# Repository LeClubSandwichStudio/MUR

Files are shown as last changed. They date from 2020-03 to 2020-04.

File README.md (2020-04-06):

# M.U.R
Minimal Universal Respirator

For more general informations about this project, see https://www.mur-project.org/

This project is under [GPLv3] (https://www.gnu.org/licenses/gpl-3.0.en.html)

## 01_MUR_OVERVIEW

Contains general documentation about the project.

## 02_MUR_HARDWARE

Contains all hardware related documentations: models, wiring, exploded views, etc

## 03_MUR_SOFTWARE

Contains Arduino based code source for the controler.

## 99_MUR_TESTS

Contains M.U.R bench marks

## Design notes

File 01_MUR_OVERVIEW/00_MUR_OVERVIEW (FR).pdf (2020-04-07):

### Minimal Universal Respirator v0.3

Aperçu général du système
(General Overview)

### INTRODUCTION

Le dispositif MUR se définit comme un équipement de respiration artificielle d'urgence. Il s’adresse au corps médical souhaitant soigner un patient atteint de SDRA (syndrome de détresse respiratoire aiguë).

Un dispositif MUR est composé respectivement d’un système matériel (“hardware”) et d’un système logiciel (“software”), pour fonctionner.

### PRINCIPE FONCTIONNEL

Sources d’entrée d’air variables.
Gestion instantanée de la pression administré au patient, par une gestion synchronisée de “fuites d’air”.

### UTILISATION

Mode ventilatoire d’usage : Pression Contrôlée (PC)

Réglages machines :
- Cycles respiratoires
- Ratio I/E
- Pression de crête
- Pression de plateau
- Pression expiratoire positive

### MATERIEL

Prérequis matériel :
- Alimentation sur secteur en 230V
- Cable usb pour communiquer avec le logiciel (optionnel)

Prérequis logiciel (optionnel, pour test et visualisation sur ordinateur) :
- Disposer d’un ordinateur avec port USB
- Avoir installé le logiciel Arduino

Le dispositif Minimal Universal Respirator (MUR) est constitué de 7 sous-ensembles distincts, qui une fois combinés, constituent le système matériel (“hardware”) d’un MUR :

1. La source d’air (FR) (https://drive.google.com/open?id=1SqGHQjwBfO2f25Swwv3l0SGI28G9KxEalMFHdRkD32M)
2. Le filtre d’entrée d’air et le régulateur de pression courante (FR) (https://drive.google.com/open?id=1I-5K1rnMSs5uvp3ED-RQ1LcxX0brZkwWDnDNk8wLztA)
3. Les valves esclaves (FR) (https://drive.google.com/open?id=1w_EUj4ocEakElgCnpraXDVv3cVOd3zsCE-9gxyla1rs)
4. Les systèmes de captations (FR) (https://drive.google.com/open?id=1ARKAw2D5dZf-3HR5xr1Ms6IWQ_QXqz-S4Hy4_T1l_os)
5. Les adaptateurs (FR) (https://drive.google.com/open?id=1K2FceapsPLCinnWBYBrEqLem5kVpyN8-s0TL2MW7GUM)
6. Le panneau de contrôle (FR) (https://drive.google.com/open?id=1XikZ0ODiRMPeeytIIQJwRYhBmEAExoJSR04DGwt4p20)
7. La tuyauterie/plomberie (FR) (https://drive.google.com/open?id=1fXODXtvYolFTmdxDlxn4JihmsS-h_IIxJIVhl_Bkw6E)

Légende (pdf)

NAME | WHAT
B Poumon de test

T Tuyaux medicaux

C1 | Capteur Pression Entrée Patient
C2 | Capteur Pression Athmosphérique
V1 | Valve esclave Entrée
S1 | Servomoteur de V1
V2 | Valve esclave Sortie
S2 | Servomoteur de V2
V3 | Valve Ressort (Echappement)
F1 | Filtre entrée D'air
CP | Paneau de contrôle

M Monitoring

A1 | Adaptor 1
A2 | Adaptor 2
A3 | Adaptor 3
FL1 | Flange 1
FL2 | Flange 2
FL3 | Flange 3

T Transformateur
Y Y

IN0 Arrivée d'air Continue

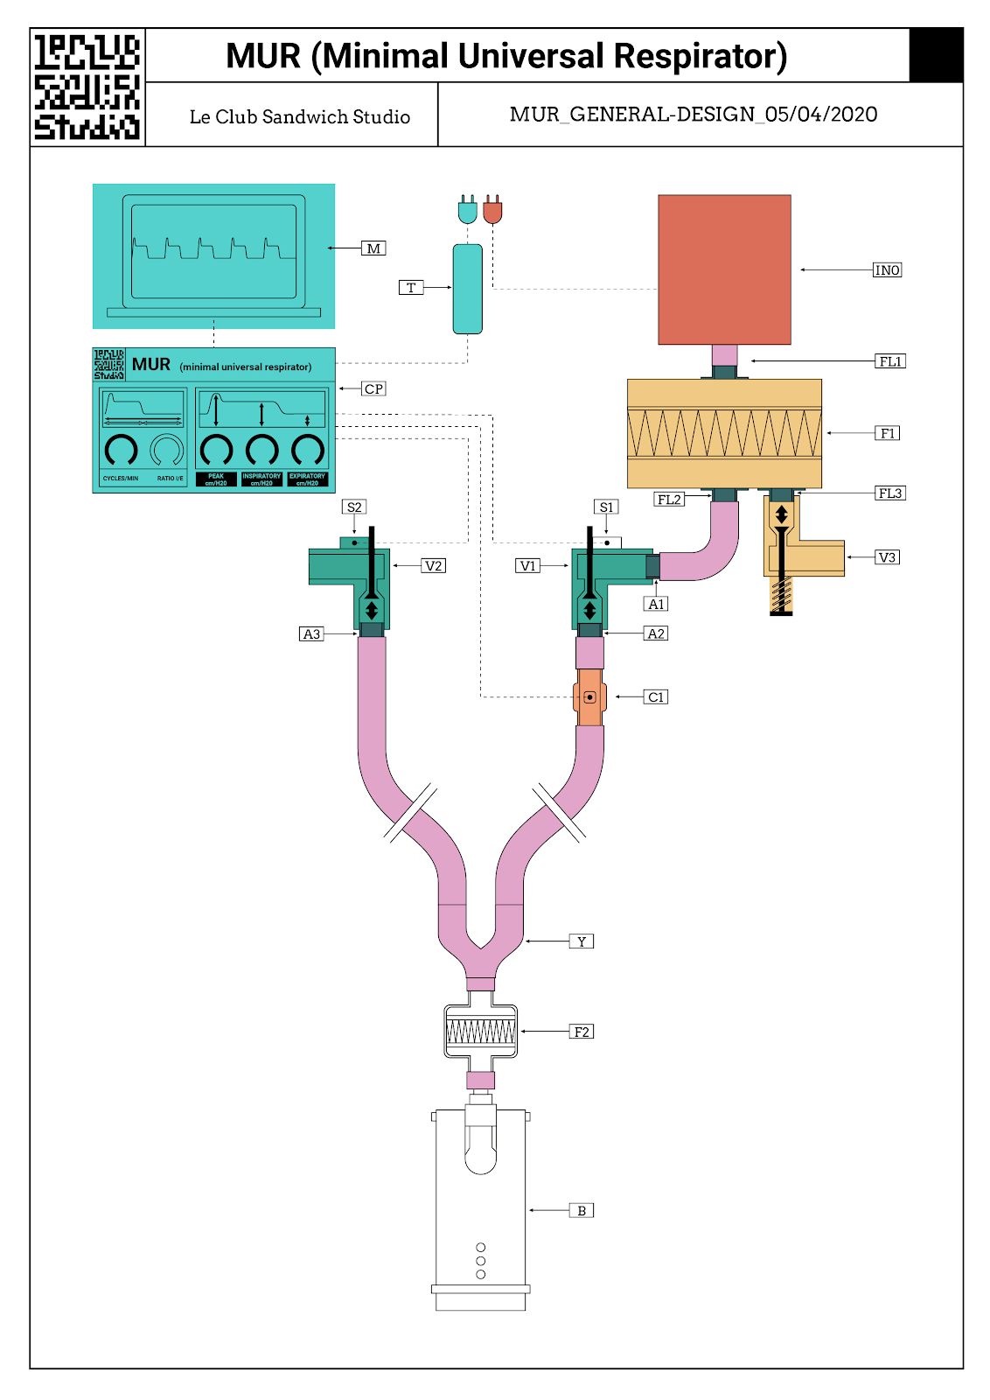
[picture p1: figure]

Design général des blocs fonctionnels (pdf) (https://drive.google.com/open?id=1_WcDWkCbM0ZlqO23SKp42NGnG-bO8ovX)

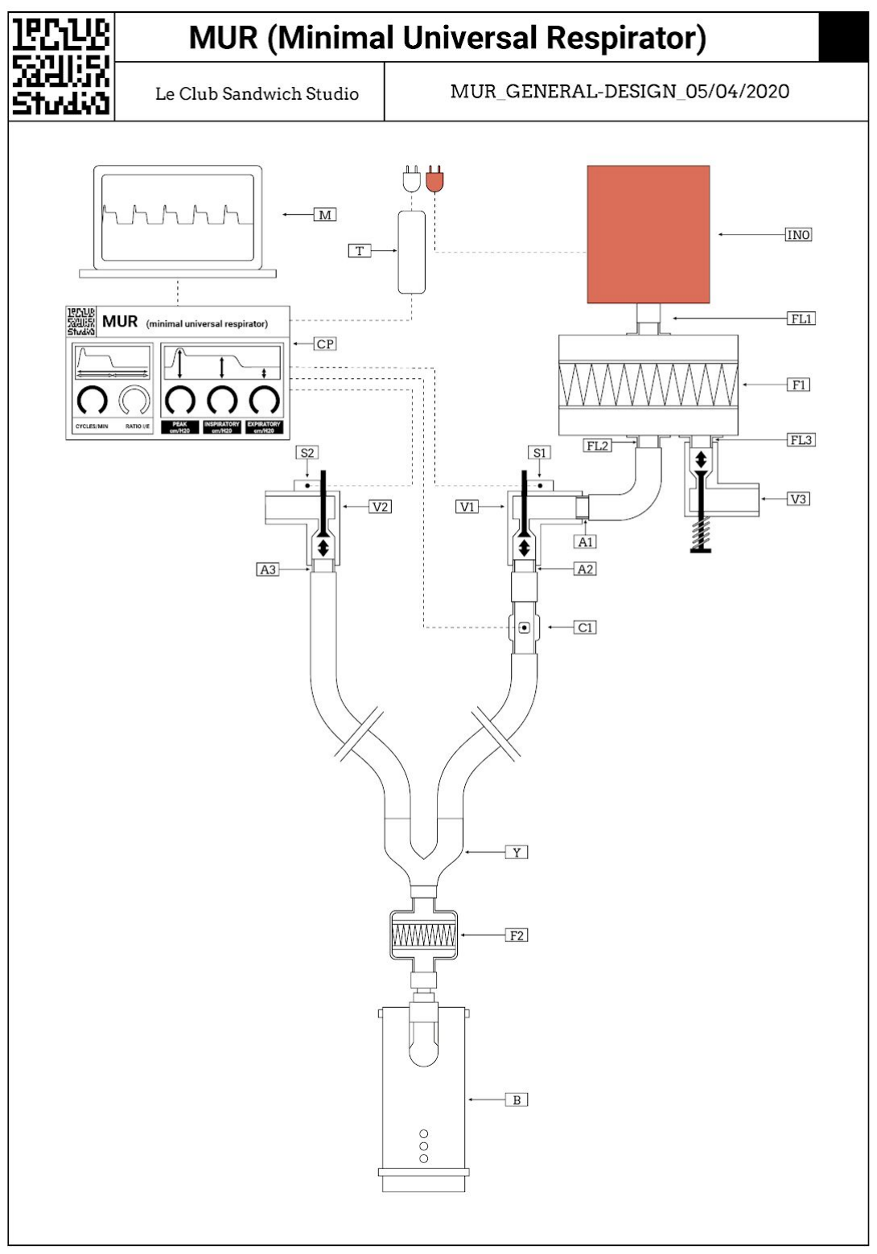
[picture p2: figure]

Design général - sous-ensemble 1 : source d’air (pdf) (https://drive.google.com/open?id=1FOaVzaCyhG92lL_MXu_-5X0B1L0EyU57)

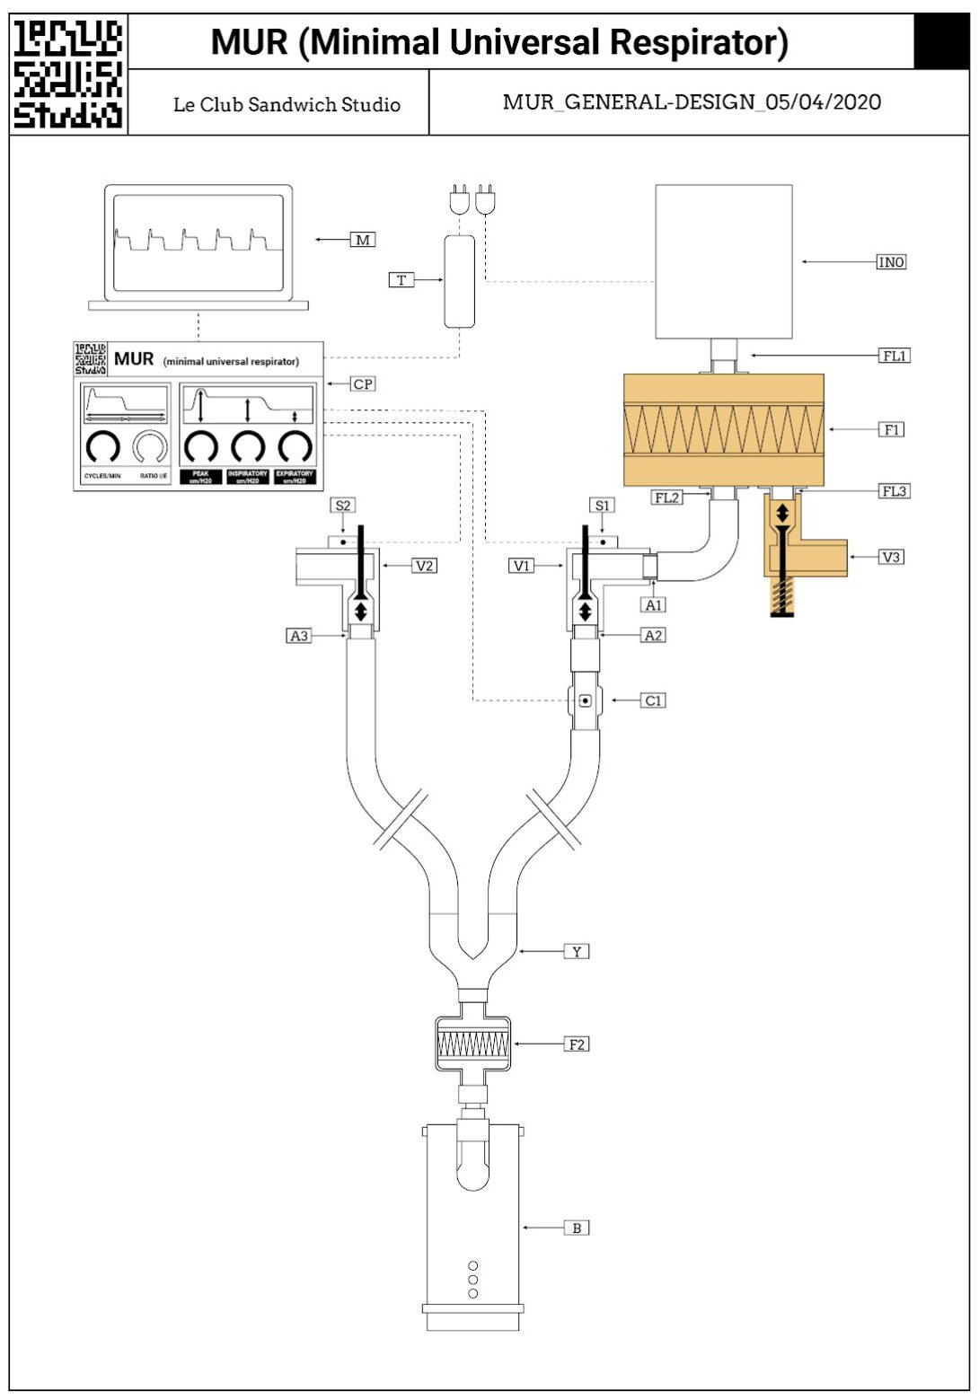
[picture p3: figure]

Design général - sous-ensemble 2 : filtre (pdf) (https://drive.google.com/open?id=1hKSTGPQz4cmegmwHS-HlvNu4kxHyBkxj)

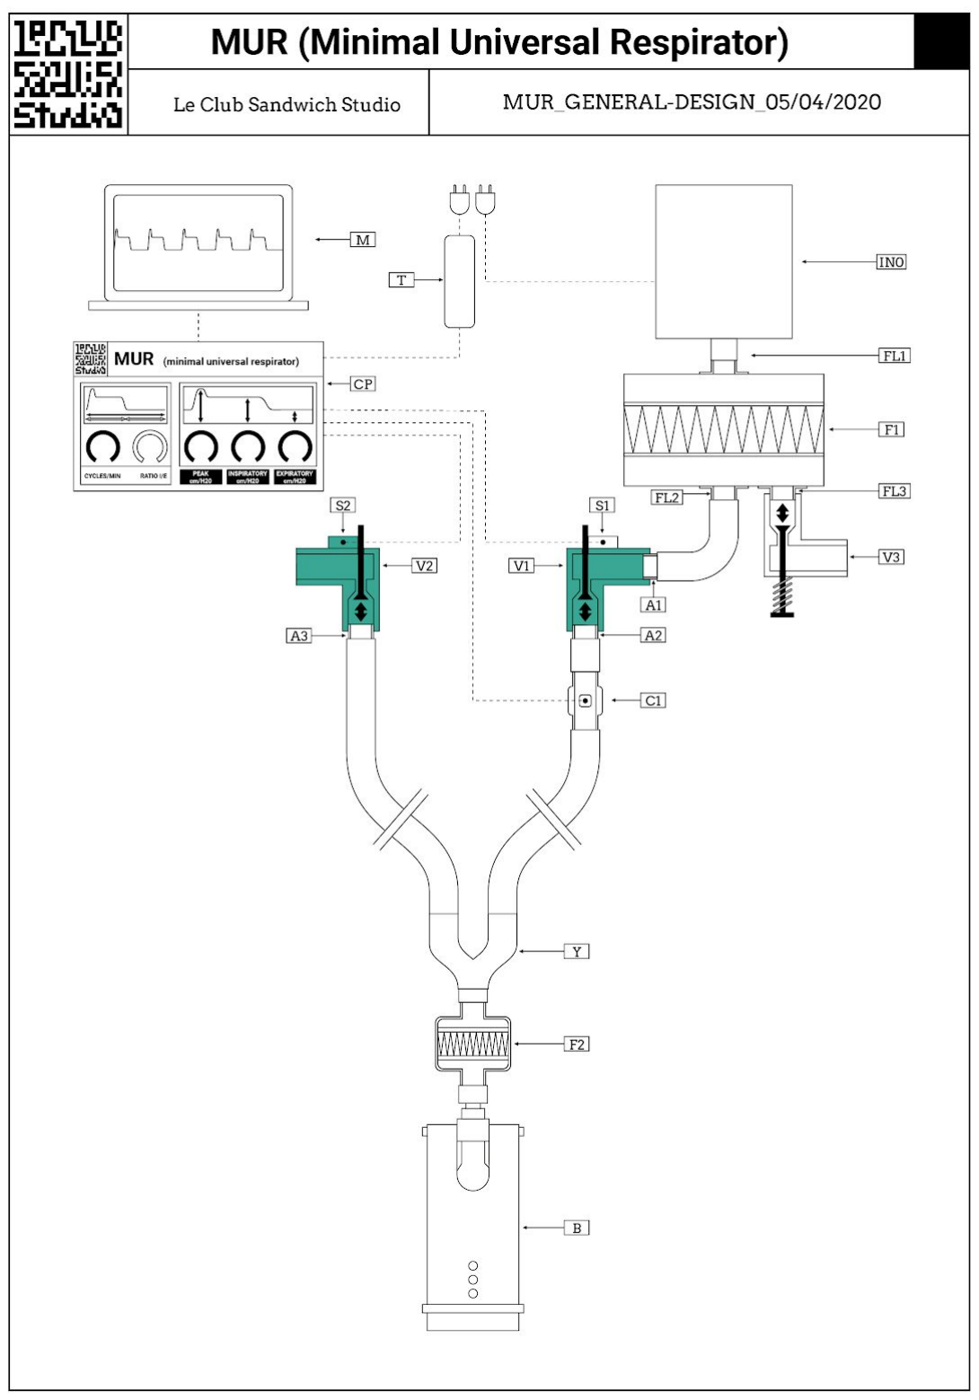
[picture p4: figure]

Design général - sous-ensemble 3 : valves (pdf) (https://drive.google.com/open?id=1HCkXBzR4LwH6LnuTaRVHANtpQzyrADqG)

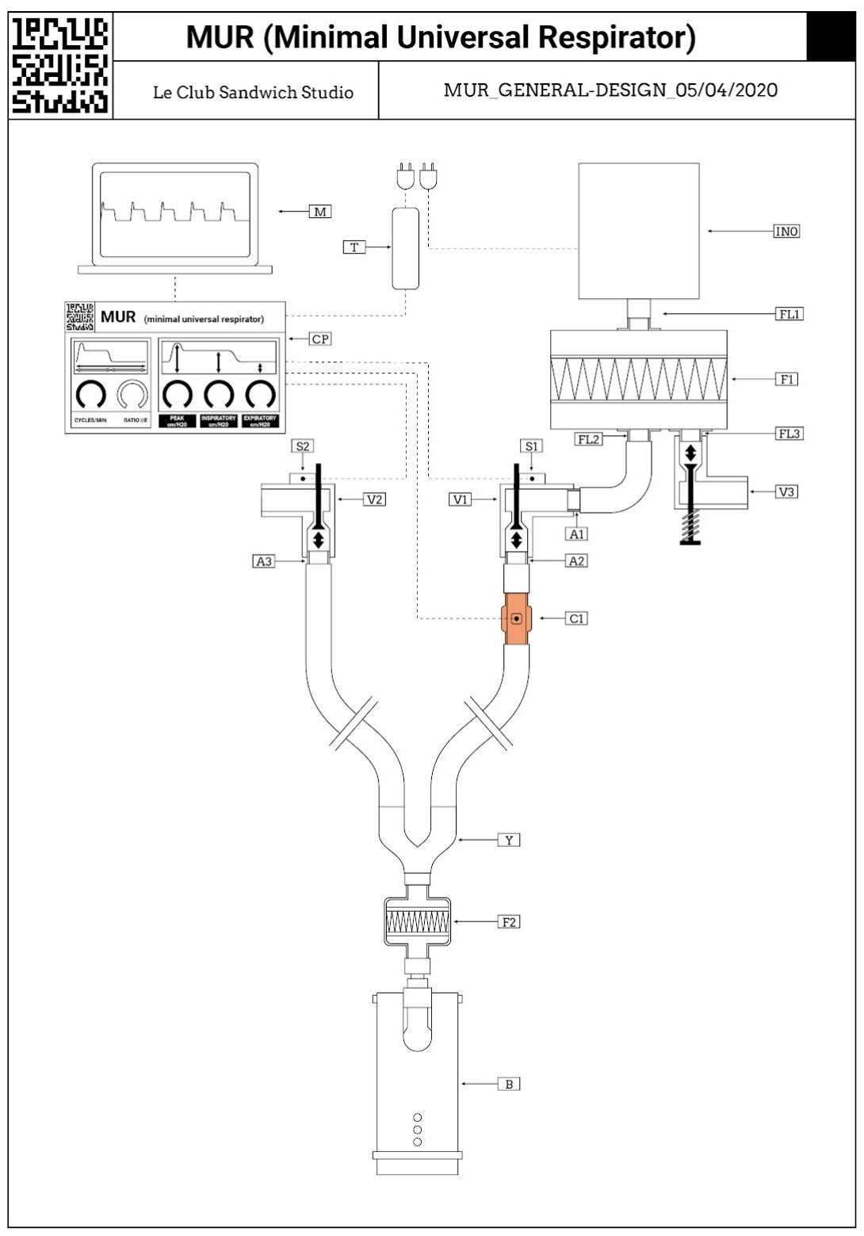
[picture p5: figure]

Design général - sous-ensemble 4 : captation (pdf) (https://drive.google.com/open?id=1NCK5aFOVgX5Ek2YtG8QKx2trs72YkA_k)

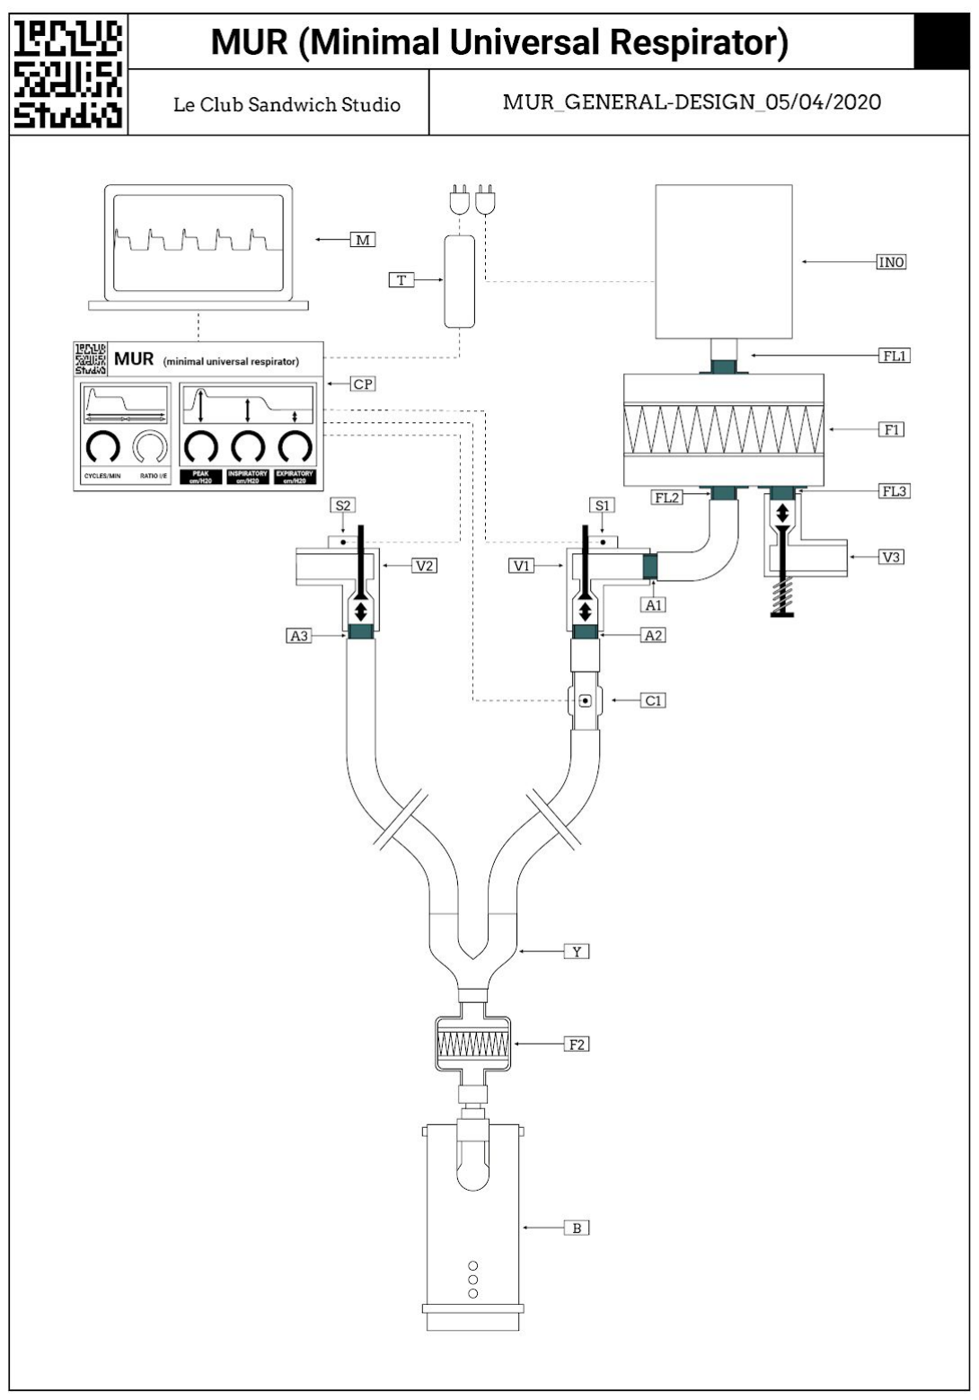
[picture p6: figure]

Design général - sous-ensemble 5 : adaptateurs (pdf) (https://drive.google.com/open?id=1cCQLFfMAgoJG9c6c1g39FGafxrEThaiq)

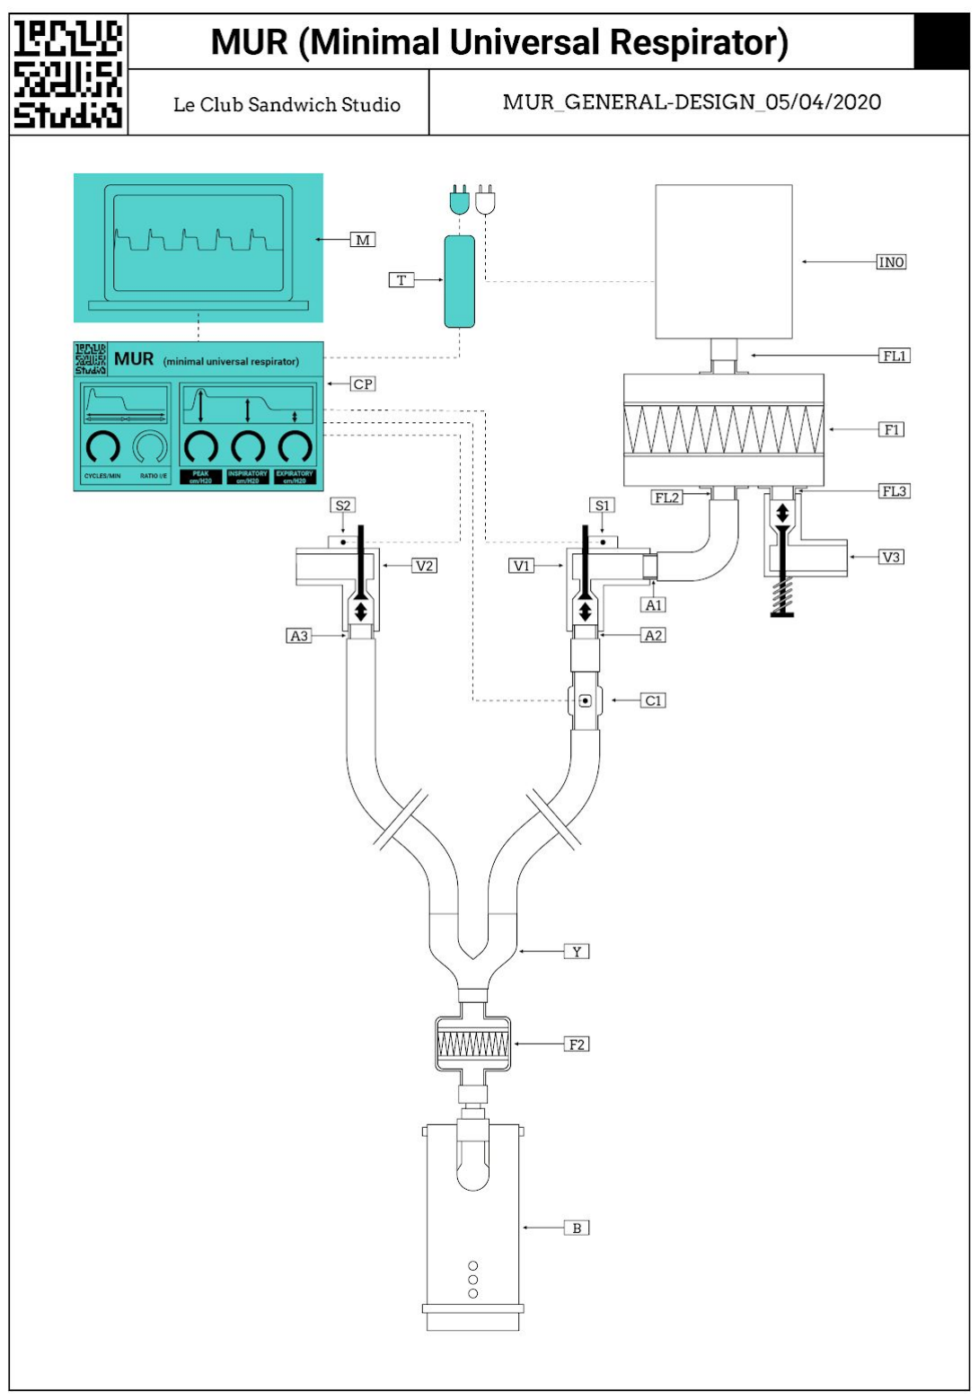
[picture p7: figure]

Design général - sous-ensemble 6 : panneau de contrôle (pdf) (https://drive.google.com/a/leclubsandwich.studio/file/d/18ofSSI9X4tlmFmg1ObH6QxRjyoEKfB24/view?usp=sharing)

### FLUX D’AIR

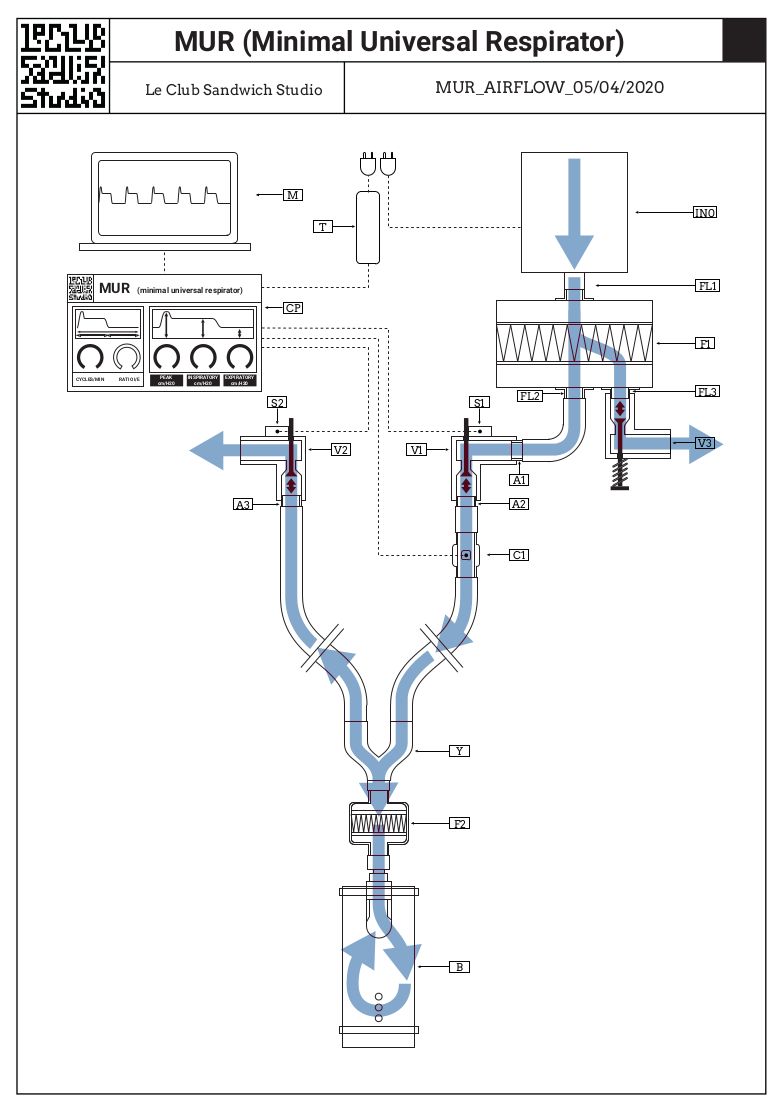
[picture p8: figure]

### LOGICIEL

### Explication fonctionnelle du code Arduino

### Présentation Générale :

Le code se veut simple, adaptable et surtout le plus stable possible.
Dans cette première version il permet des réglages de respiration qui sont les mêmes que les réglages utilisé par le corps médical. Le but n’est pas de faire preuve d’innovation à ce sujet mais d’accompagner les soignants au plus proche de leurs connaissances.

### Fonctionnalités :

Un code Arduino, simple et efficace apte à ventiler une personne sédaté dans une structure permettant d’accueillir des malades Covid-19. Code largement commenté directement sur Arduino.

- Cinqs potentiomètres pour simplement et précisément régler le cycle de respiration
- Cycles par minute
- Ratio Inspiration/Expiration (I/E)
- Pression peak a l’inspiration
- Pression plateau pendant l’inspiration
- Pression PEEP pendant l’expiration
- Deux interrupteurs à glissière pour des fonctions de réglage et de maintenance
- Maintenance pour mettre les deux servos à 0° (position fermé) pour le montage
- Calibration pour régler la pression maximale dans le circuit
La routine de réglage des valves et de la pression est détaillé dans le code Arduino.
- Deux capteurs de température/pression/humidité d’air bosch BME280.
- Dans le circuit d’air après la valve d'entrée (C1)
- Un deuxième capteur pour la pression atmosphérique ambiant (C2)

- “Monitoring” à travers le traceur serial inclue dans la Arduino IDE. Ce logiciel est gratuit et existe pour quasiment tous les systèmes d’exploitation au monde.
- Pression dans le circuit d’air (bleu en CmH20)
- Position de la valve d’entrée
- Position de la Valve de sortie
- Alarme qui réagit & la suppression. (buzzer et led)
- peakAlarmLevel = 40mbar
- plateauAlarmLevel = 30mbar

### SCHEMA DE CABLAGE

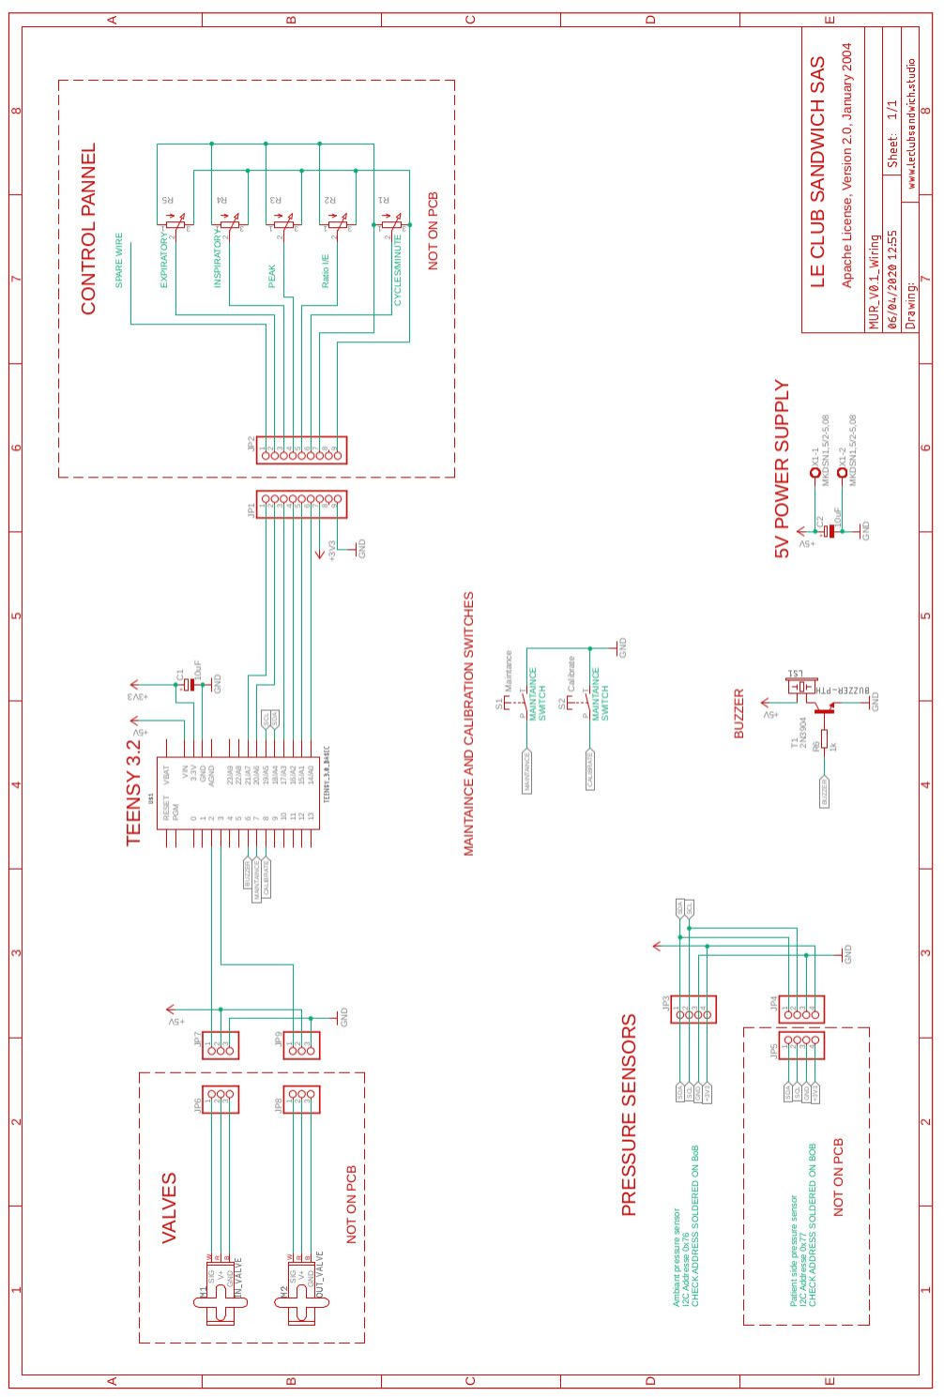
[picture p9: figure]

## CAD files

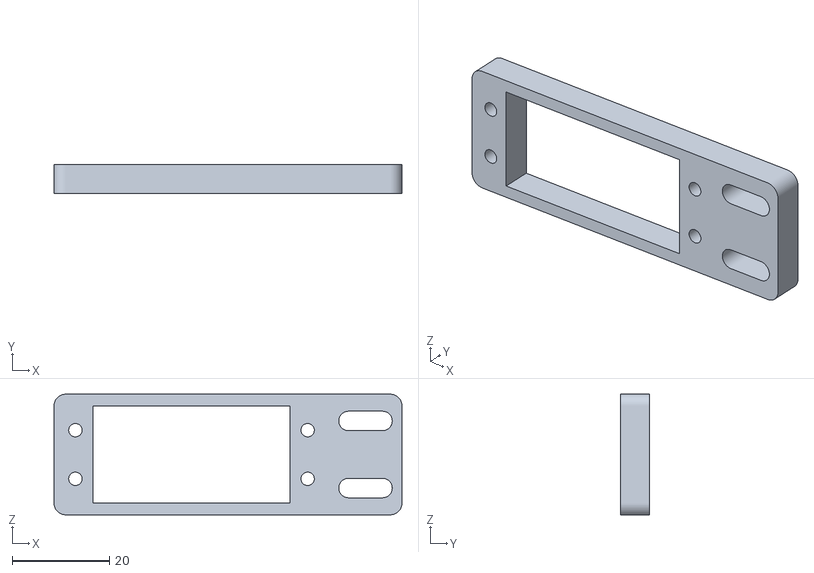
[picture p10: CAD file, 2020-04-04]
02_MUR_HARDWARE/models/v0.3/ServoHolder.stl
71.5 x 6.00 x 24.8

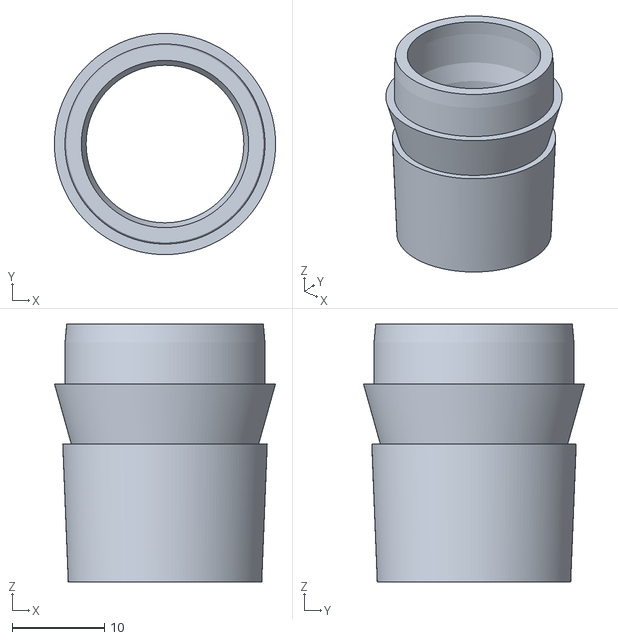
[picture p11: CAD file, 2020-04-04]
02_MUR_HARDWARE/models/v0.3/Adaptor_X2.stl
24.0 x 24.0 x 28.0

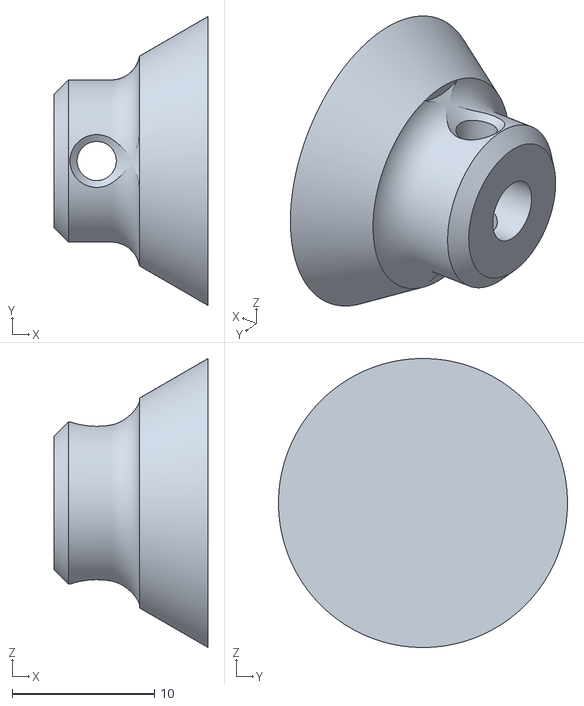
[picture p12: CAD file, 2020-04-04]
02_MUR_HARDWARE/models/v0.3/Valve_Piston.stl
10.8 x 20.3 x 20.3

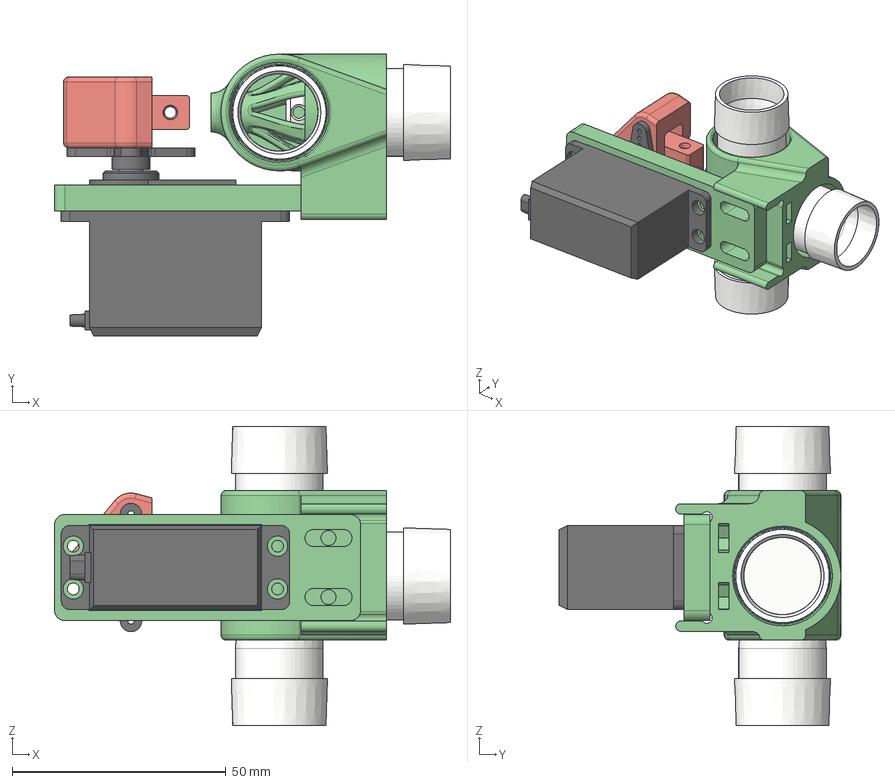
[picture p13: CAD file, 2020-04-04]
02_MUR_HARDWARE/models/v0.3/ValveV3.1 v5.step
92.6 x 65.9 x 70.0 mm

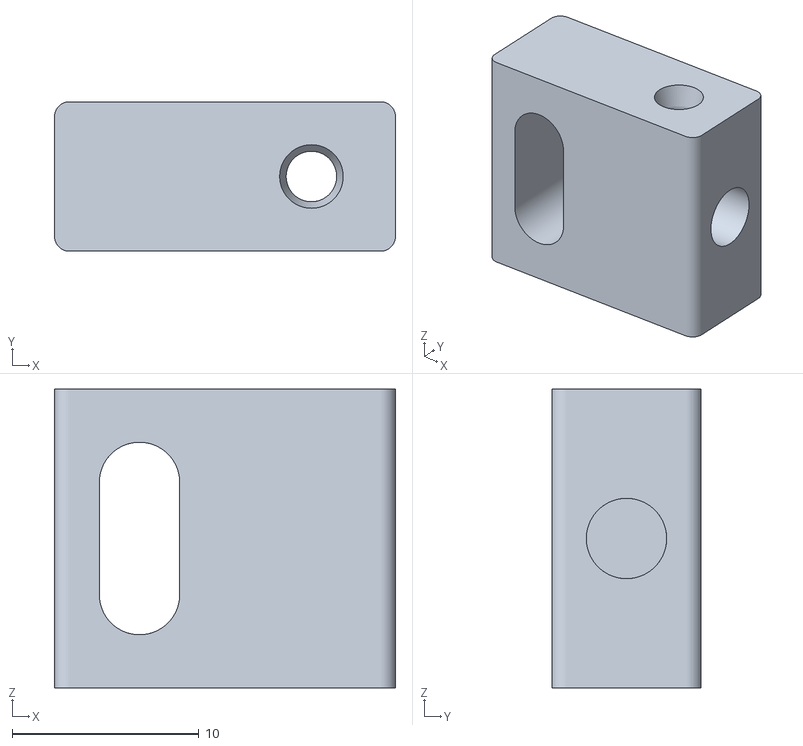
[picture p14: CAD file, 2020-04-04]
02_MUR_HARDWARE/models/v0.3/Valve_Pusher.stl
18.2 x 8.00 x 16.0

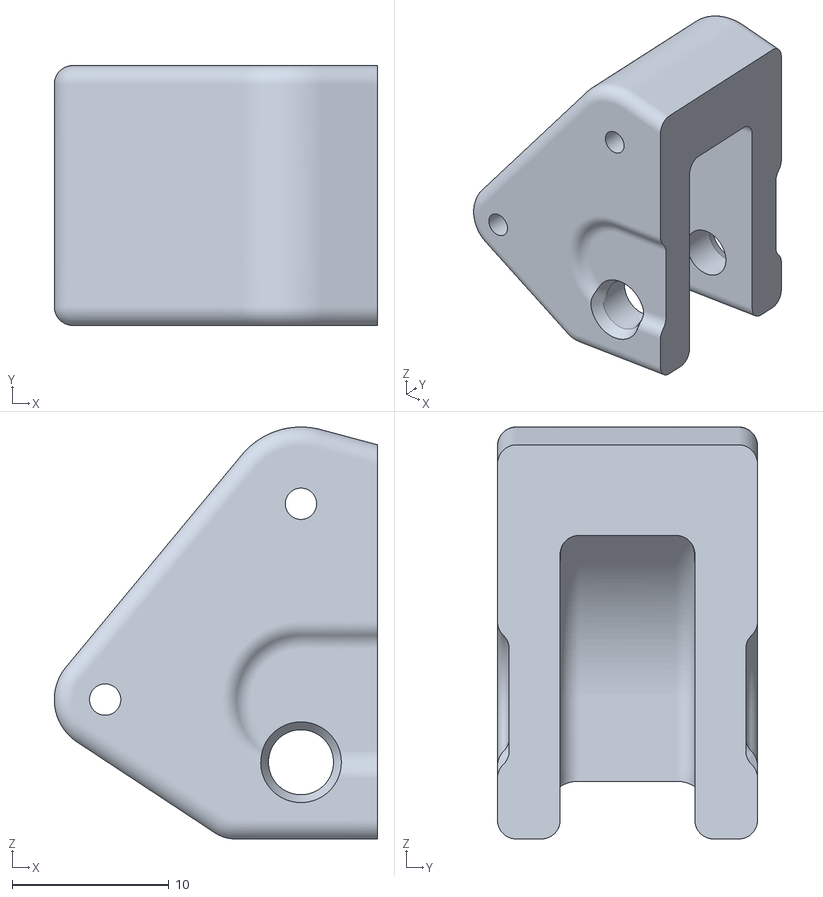
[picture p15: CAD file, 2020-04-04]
02_MUR_HARDWARE/models/v0.3/Servo_Lever.stl
20.7 x 16.6 x 26.3

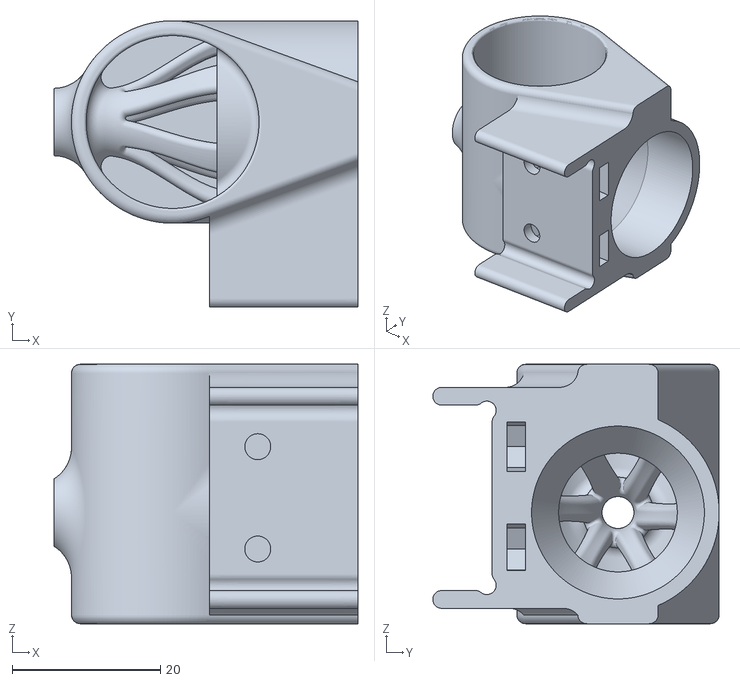
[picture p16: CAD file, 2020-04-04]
02_MUR_HARDWARE/models/v0.3/Valve_Body.stl
41.0 x 38.6 x 35.0

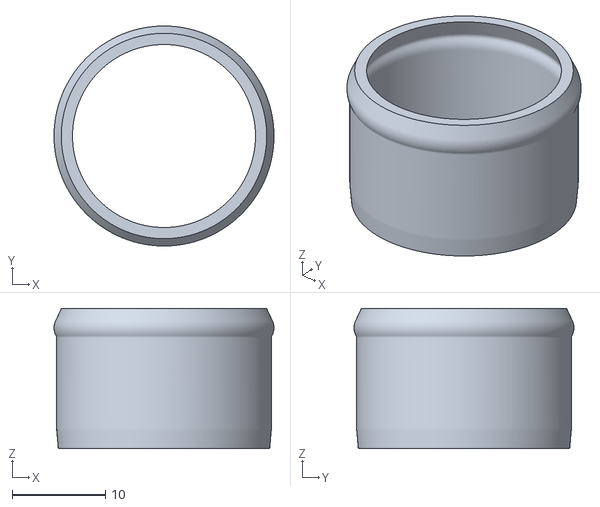
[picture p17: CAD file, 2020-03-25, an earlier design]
02_MUR_HARDWARE/models/v0.1/3D_ExportSTL/Adaptor_X3.stl
23.6 x 23.6 x 15.0

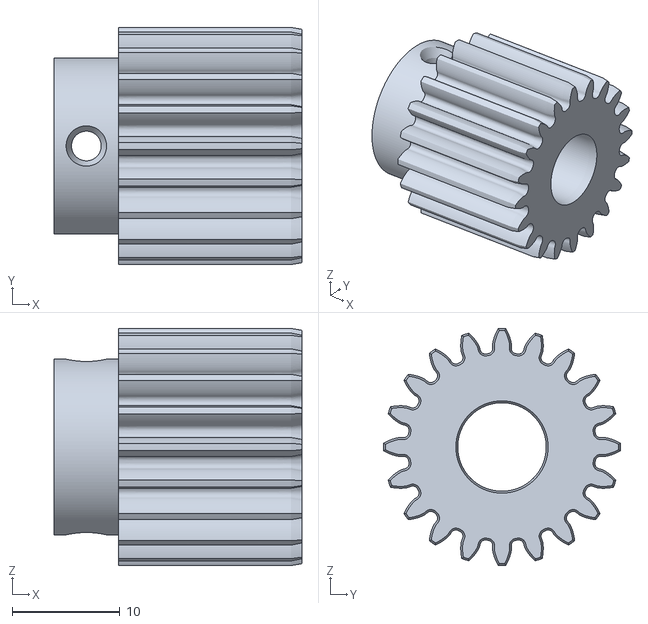
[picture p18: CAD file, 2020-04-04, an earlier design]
02_MUR_HARDWARE/models/v0.2.1/Pinion_20.stl
23.0 x 22.0 x 22.0

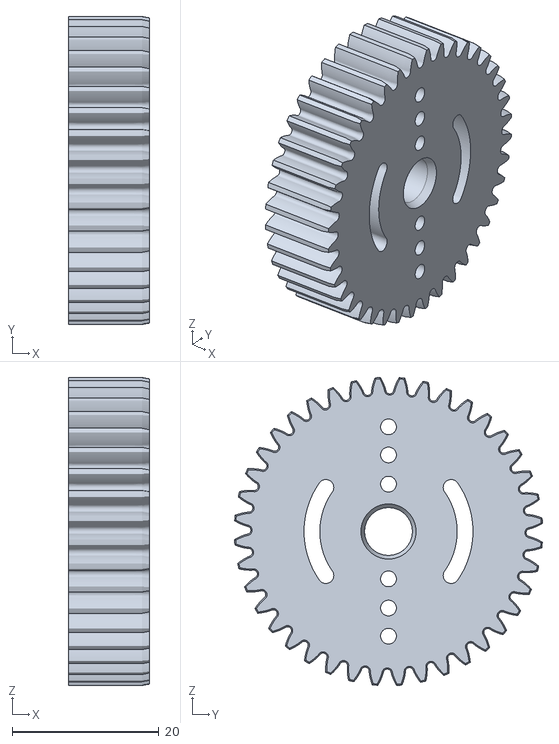
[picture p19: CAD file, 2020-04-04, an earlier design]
02_MUR_HARDWARE/models/v0.2.2/Spur_40.stl
11.0 x 41.9 x 41.9

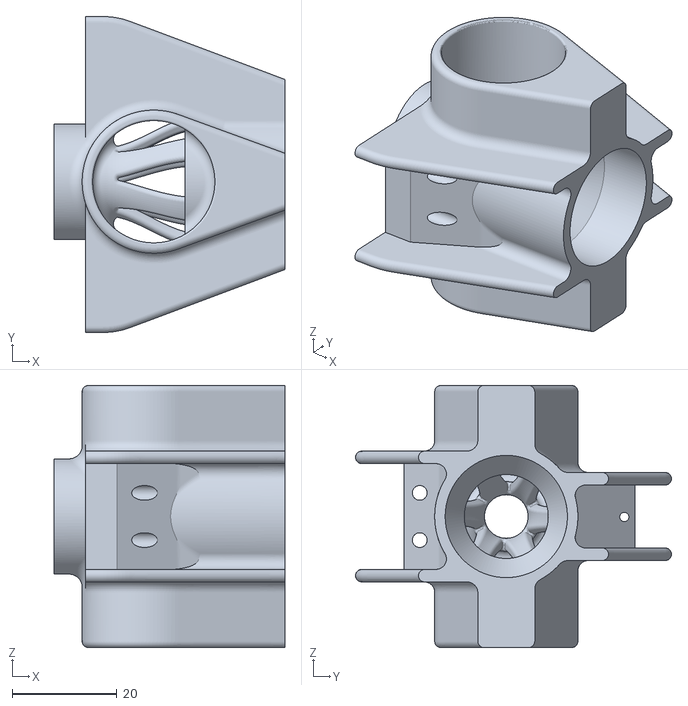
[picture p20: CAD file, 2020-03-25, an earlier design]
02_MUR_HARDWARE/models/v0.1/3D_ExportSTL/Valve_Body.stl
44.0 x 60.2 x 50.0

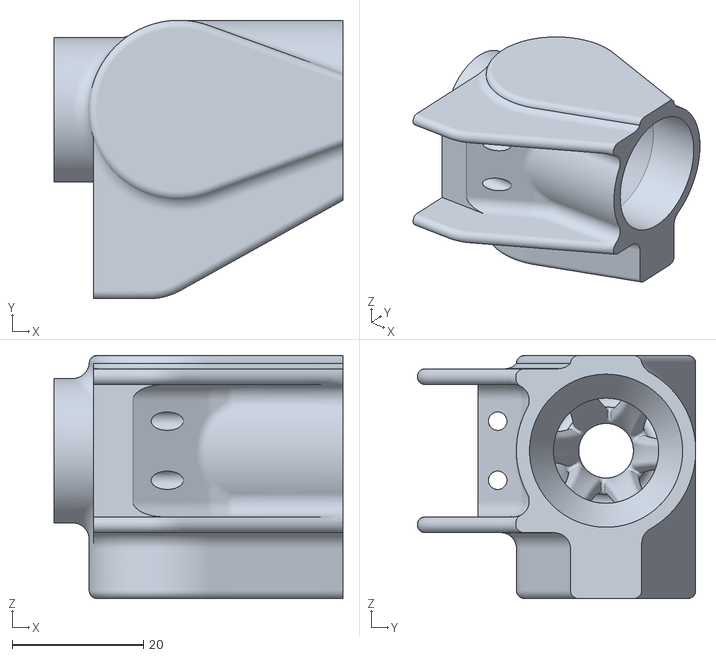
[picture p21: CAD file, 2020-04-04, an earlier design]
02_MUR_HARDWARE/models/v0.2.1/Valve_Body.stl
44.0 x 42.4 x 37.0

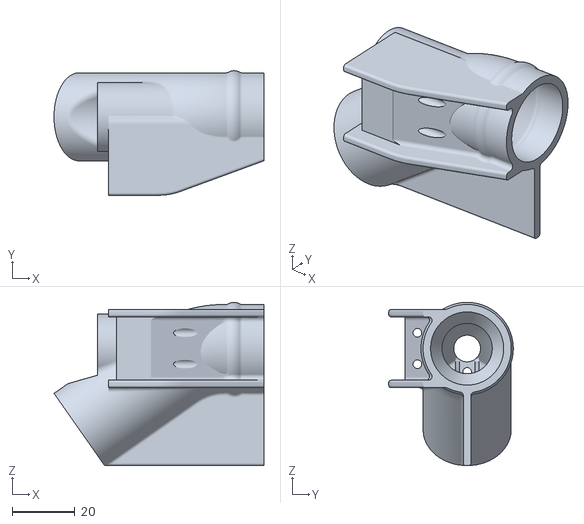
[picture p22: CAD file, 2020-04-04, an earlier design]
02_MUR_HARDWARE/models/v0.2.2/Valve_Body 2.2.stl
66.9 x 39.7 x 52.0

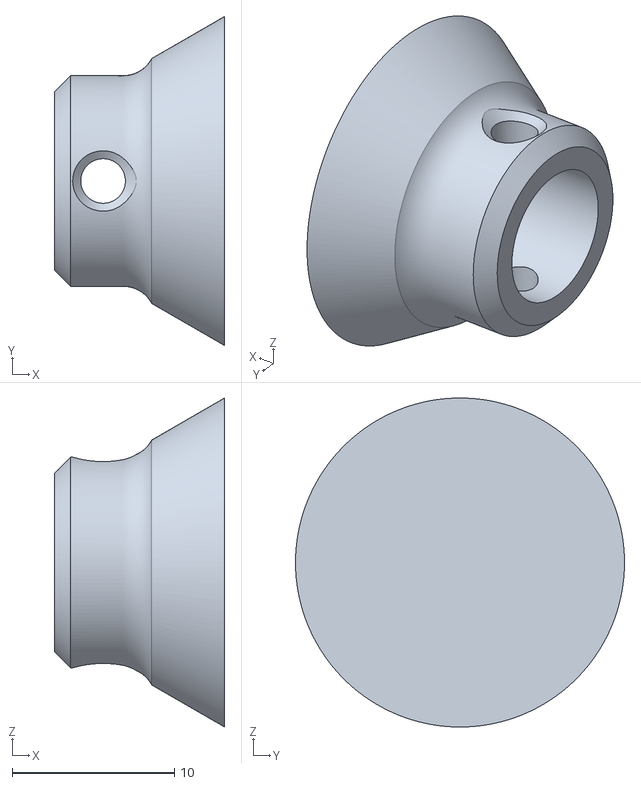
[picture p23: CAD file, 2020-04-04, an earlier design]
02_MUR_HARDWARE/models/v0.2.2/Valve_Piston.stl
10.5 x 20.3 x 20.3

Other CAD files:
02_MUR_HARDWARE/models/v0.1/3D_ExportSTL/Spur_40.stl
02_MUR_HARDWARE/models/v0.2.1/Spur_40.stl
02_MUR_HARDWARE/models/v0.1/3D_ExportSTL/Pinion_20.stl
02_MUR_HARDWARE/models/v0.2.1/Valve_Piston.stl
02_MUR_HARDWARE/models/v0.1/3D_ExportSTL/Valve_Piston.stl
02_MUR_HARDWARE/models/v0.2.2/Pinion_20.stl
02_MUR_HARDWARE/models/v0.2/V2.0_MetalScrew/Adaptor_X3.stl
02_MUR_HARDWARE/models/v0.2/V2.0_MetalScrew/Spur_40.stl
02_MUR_HARDWARE/models/v0.2/V2.0_MetalScrew/Valve_Body.stl
02_MUR_HARDWARE/models/v0.2/V2.0_MetalScrew/Valve_Piston.stl
02_MUR_HARDWARE/models/v0.2/V2.0_MetalScrew/Valve_Piston_Oring.stl
02_MUR_HARDWARE/models/v0.2/V2.0_PrintedScrew/Adaptor_X3.stl
02_MUR_HARDWARE/models/v0.2/V2.0_PrintedScrew/Pinion_20.stl
02_MUR_HARDWARE/models/v0.2/V2.0_PrintedScrew/Spur_40.stl
02_MUR_HARDWARE/models/v0.2/V2.0_PrintedScrew/Valve_Body.stl
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

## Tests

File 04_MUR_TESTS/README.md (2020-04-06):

This folder contains tests done on bench test equipment by bio-medical engineers.

Date and location is contained in the sub-folder names.

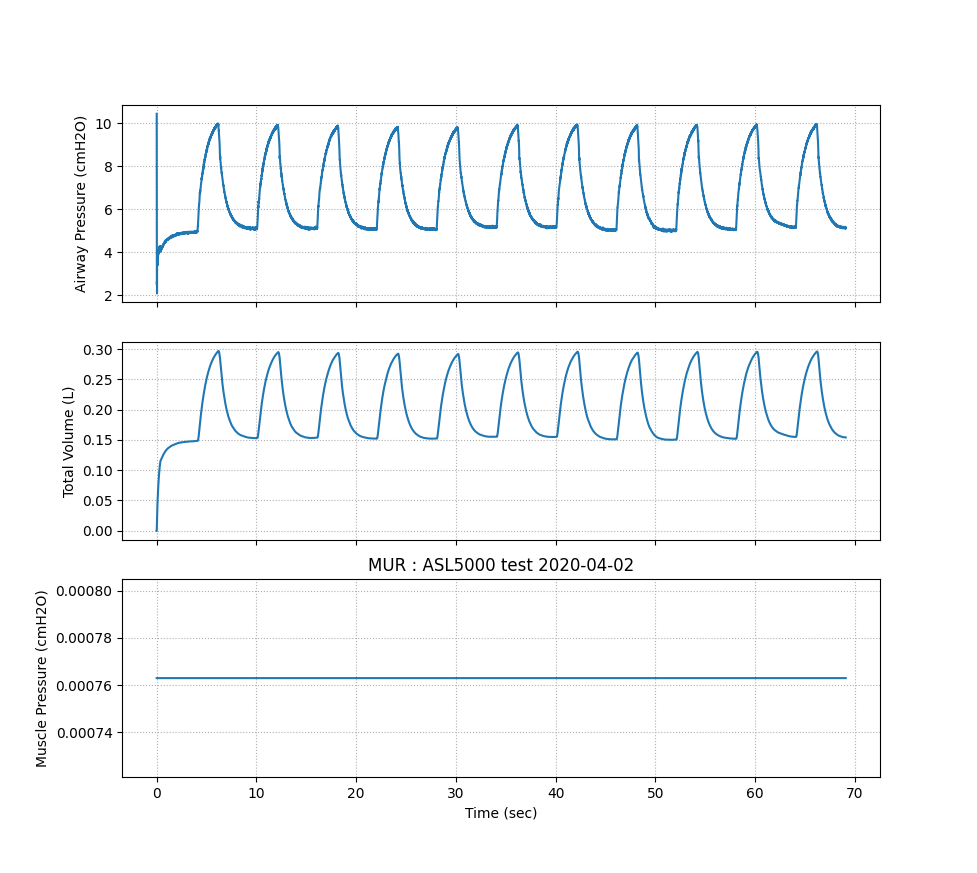
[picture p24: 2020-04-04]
04_MUR_TESTS/2020-03-27-ASL5000-Mondor/test_2.png

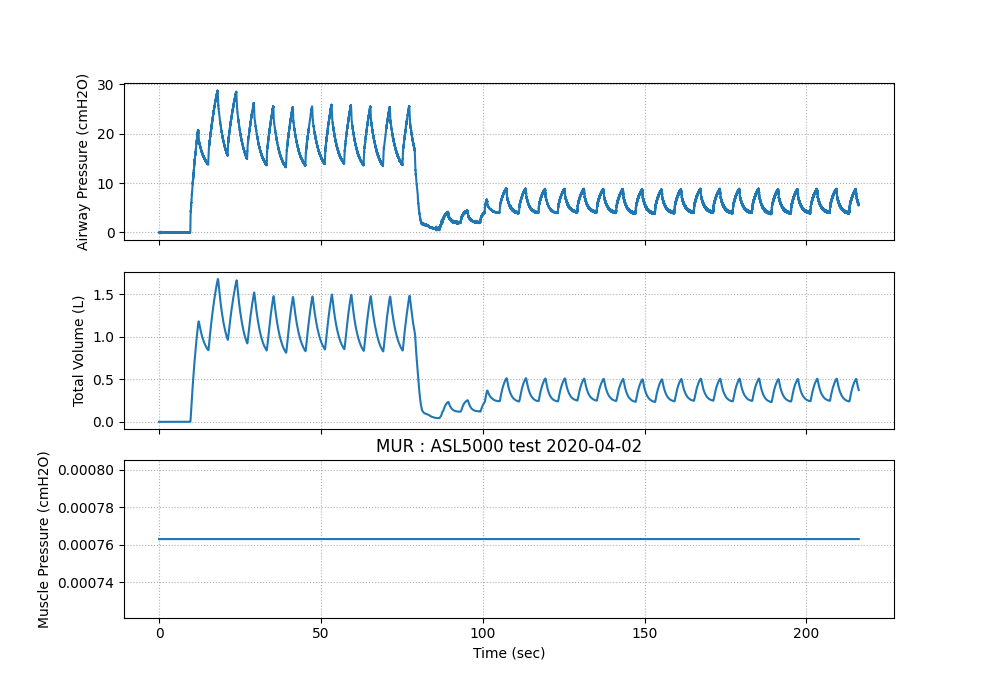
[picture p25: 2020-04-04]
04_MUR_TESTS/2020-03-27-ASL5000-Mondor/test_1.png

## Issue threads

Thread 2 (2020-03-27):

### ISSUE TITLE
In the first comment there seem to be a typo between 180 and 160

### ISSUE THREAD

**Issue by MCMic** [LeClubSandwichStudio/MUR#2]
Maybe I misunderstood but it seems to me lines 52/53 should state 180 like the ones before and after, or the other ones are wrong and should state 160 as well, not sure?

https://github.com/LeClubSandwichStudio/MUR/blob/d80a23c6057c3697014bc0ded8df49dc8f256d1d/V0/software/MUR.ino#L52

**Comment by LeSuedois** [comment]
Hello,
sorry but this value is still in work in progress. We started with 180° and lowered it to 60° now with our new (and better) airvalves. another positive aspect is that the movement is much faster and reduced wear on those cheap servos. 
As written in the comments this value changes from servo to servo and must be tweaked to match your hardware!

**Comment by LeSuedois** [comment]
please wait for major update coming this weekend. we only publish once tested in medical environment

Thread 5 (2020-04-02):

### ISSUE TITLE
compatibility issues with .stl files

### ISSUE THREAD

**Issue by DelphineRoy** [LeClubSandwichStudio/MUR#5]
Could not read the .stl files on my version of cura (4.1.0). They should be readable with any version. Couldn't open it with Windows' stl reader either, nor with sketchup. Windows 3D Builder returned the message "Couldn't load that. Error code: 0x80004005".

**Comment by LeSuedois** [comment]
hmm we don't have problems with our stl files under fusion 360 and prusa slicer...
Many people with other softwares printed out files without problem. I think the problem is on your side, so I close this issue.
Please try with other software. Sketchup is marvelous for "big" stuff and architecture!

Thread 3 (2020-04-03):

### ISSUE TITLE
Maybe you made an error ?

### ISSUE THREAD

**Issue by KennnyTroll** [LeClubSandwichStudio/MUR#3]
Hello!
Maybe you made an error on V0.1 the last argument in the Adafruit_BME280 function
bmePatient.setSampling (1, 1, 3, 1, 1, 10);
and
bmeAmbient.setSampling (1, 1, 3, 1, 1, 10);
because I had to make a modification in your code to bring it to Visual Studio
bmePatient.setSampling (1, 1, 3, 1, 1, 6);
bmeAmbient.setSampling (1, 1, 3, 1, 1, 6);

and visual studio do not accept int values for the setSampling function

I had to replace with

.setSampling (
      Adafruit_BME280 :: sensor_mode :: MODE_FORCED ,// = 1
      Adafruit_BME280 :: sensor_sampling :: SAMPLING_X1 ,// = 1
      Adafruit_BME280 :: sensor_sampling :: SAMPLING_X4 ,// = 3
      Adafruit_BME280 :: sensor_sampling :: SAMPLING_X1 ,// = 1
      Adafruit_BME280 :: sensor_filter :: FILTER_X2 ,// = 1
      Adafruit_BME280 :: standby_duration :: STANDBY_MS_10 //STANDBY_MS_10 = 6      10 not exists !!
      );

For information:
enum standby_duration {
    STANDBY_MS_0_5 = 0b000, // = 0
    STANDBY_MS_10 = 0b110, // = 6
    STANDBY_MS_20 = 0b111, // = 7
    STANDBY_MS_62_5 = 0b001, // = 1
    STANDBY_MS_125 = 0b010, // = 2
    STANDBY_MS_250 = 0b011, // = 3
    STANDBY_MS_500 = 0b100, // = 4
    STANDBY_MS_1000 = 0b101 // = 5
  };

I hope I'm not mistaken, and that it helps you ...

I do not yet have a BME280 sensor to try this code at home but I am trying to create a U-tube manometers with salt water ...

Good luck to all! And thanks for everything !

**Comment by fpistm** [comment]
Hi, 
I confirm the issue raised by @KennnyTroll.
Using enum type is better to ensure to not use a wrong value which is the case here.

**Comment by LeSuedois** [comment]
Thank you guys, indeed I did a mistake...
I try to check this out this afternoon, but most time this week was spent to sourcing parts and talking to people.....
We are in  a hurry since 3 weeks and it's clear that no one in this wokshop is a professional embedded software developer. I only do stuff that works (search for "lesuedois" on google)..
Please feel free to do a pull request if you see stuff I messed up!
This is IMO the fastest way to help me!
Thank you!

**Comment by KennnyTroll** [comment]
Pull requests sent !

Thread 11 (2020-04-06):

### ISSUE TITLE
please

### ISSUE THREAD

**Issue by devoss62** [LeClubSandwichStudio/MUR#11]
Hello,

missing the pusher and a guide piece?

Sylvain,

![ValveV4 0-v40](https://user-images.githubusercontent.com/55943394/78366554-f56db600-75c0-11ea-9673-5c977fea48ad.png)

**Comment by cquest** [comment]
The pusher is not 3D printed. We're about to publish a much more detailed set of documents (WIP).

**Comment by DoubleCigogne** [comment]
These parts are in the BOM and they are not 3D Printed. 
They are :
- T8x4 screw from a 3D printer
- T8x4 Brass nut from a 3D printer

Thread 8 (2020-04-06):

### ISSUE TITLE
Bill of Materials

### ISSUE THREAD

**Issue by Jacoby6000** [LeClubSandwichStudio/MUR#8]
For people to start building these rapidly in local communities, it would be helpful to have a BOM in CSV form which people can reference for when they're gathering supplies.  Here's an example of what I mean:  https://docs.google.com/spreadsheets/d/1Eib0IkmRiP-zVM2p6gZ9PJ2bsDDvSKWbGtUybuFWfcs/edit#gid=1276357080

I'll start working on putting this together in my freetime when I can.

**Comment by LeSuedois** [comment]
Please wait a bit... We are finishing the documentation and update master soon.
BTW, I know what's CSV...

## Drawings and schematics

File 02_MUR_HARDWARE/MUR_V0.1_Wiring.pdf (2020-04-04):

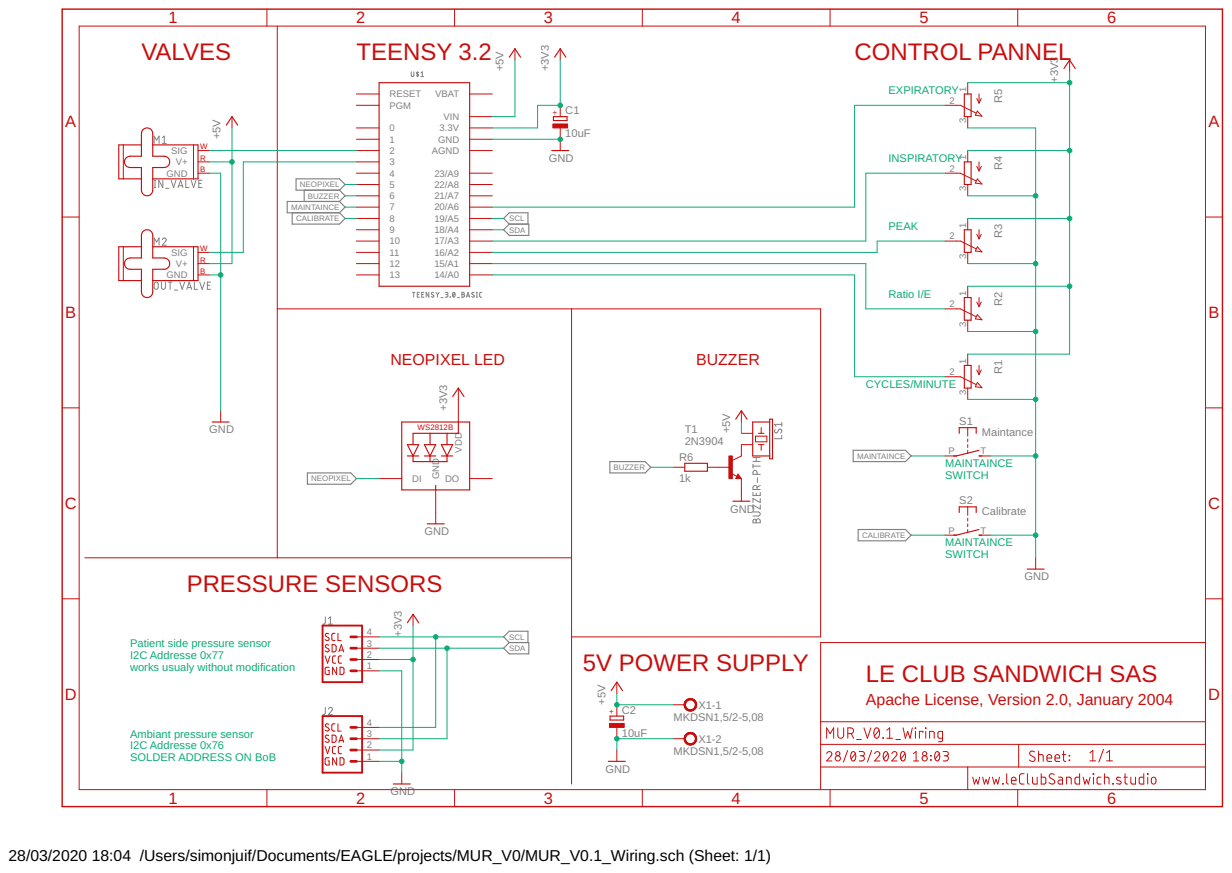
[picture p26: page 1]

VALVES

Patient side pressure sensor
I2C Addresse 0x77 works usualy without modification Ambiant pressure sensor

LE CLUB SANDWICH SAS
Apache License, Version 2.0, January 2004

I2C Addresse 0x76
SOLDER ADDRESS ON BoB

28/03/2020 18:04 /Users/simonjuif/Documents/EAGLE/projects/MUR_V0/MUR_V0.1_Wiring.sch (Sheet: 1/1)

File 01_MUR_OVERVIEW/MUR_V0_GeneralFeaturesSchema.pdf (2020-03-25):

### MUR_V0_FUNCTIONAL DIAGRAM_24/02/2020 C+7 DAYS (24/03/2020) Le Club Sandwich Studio

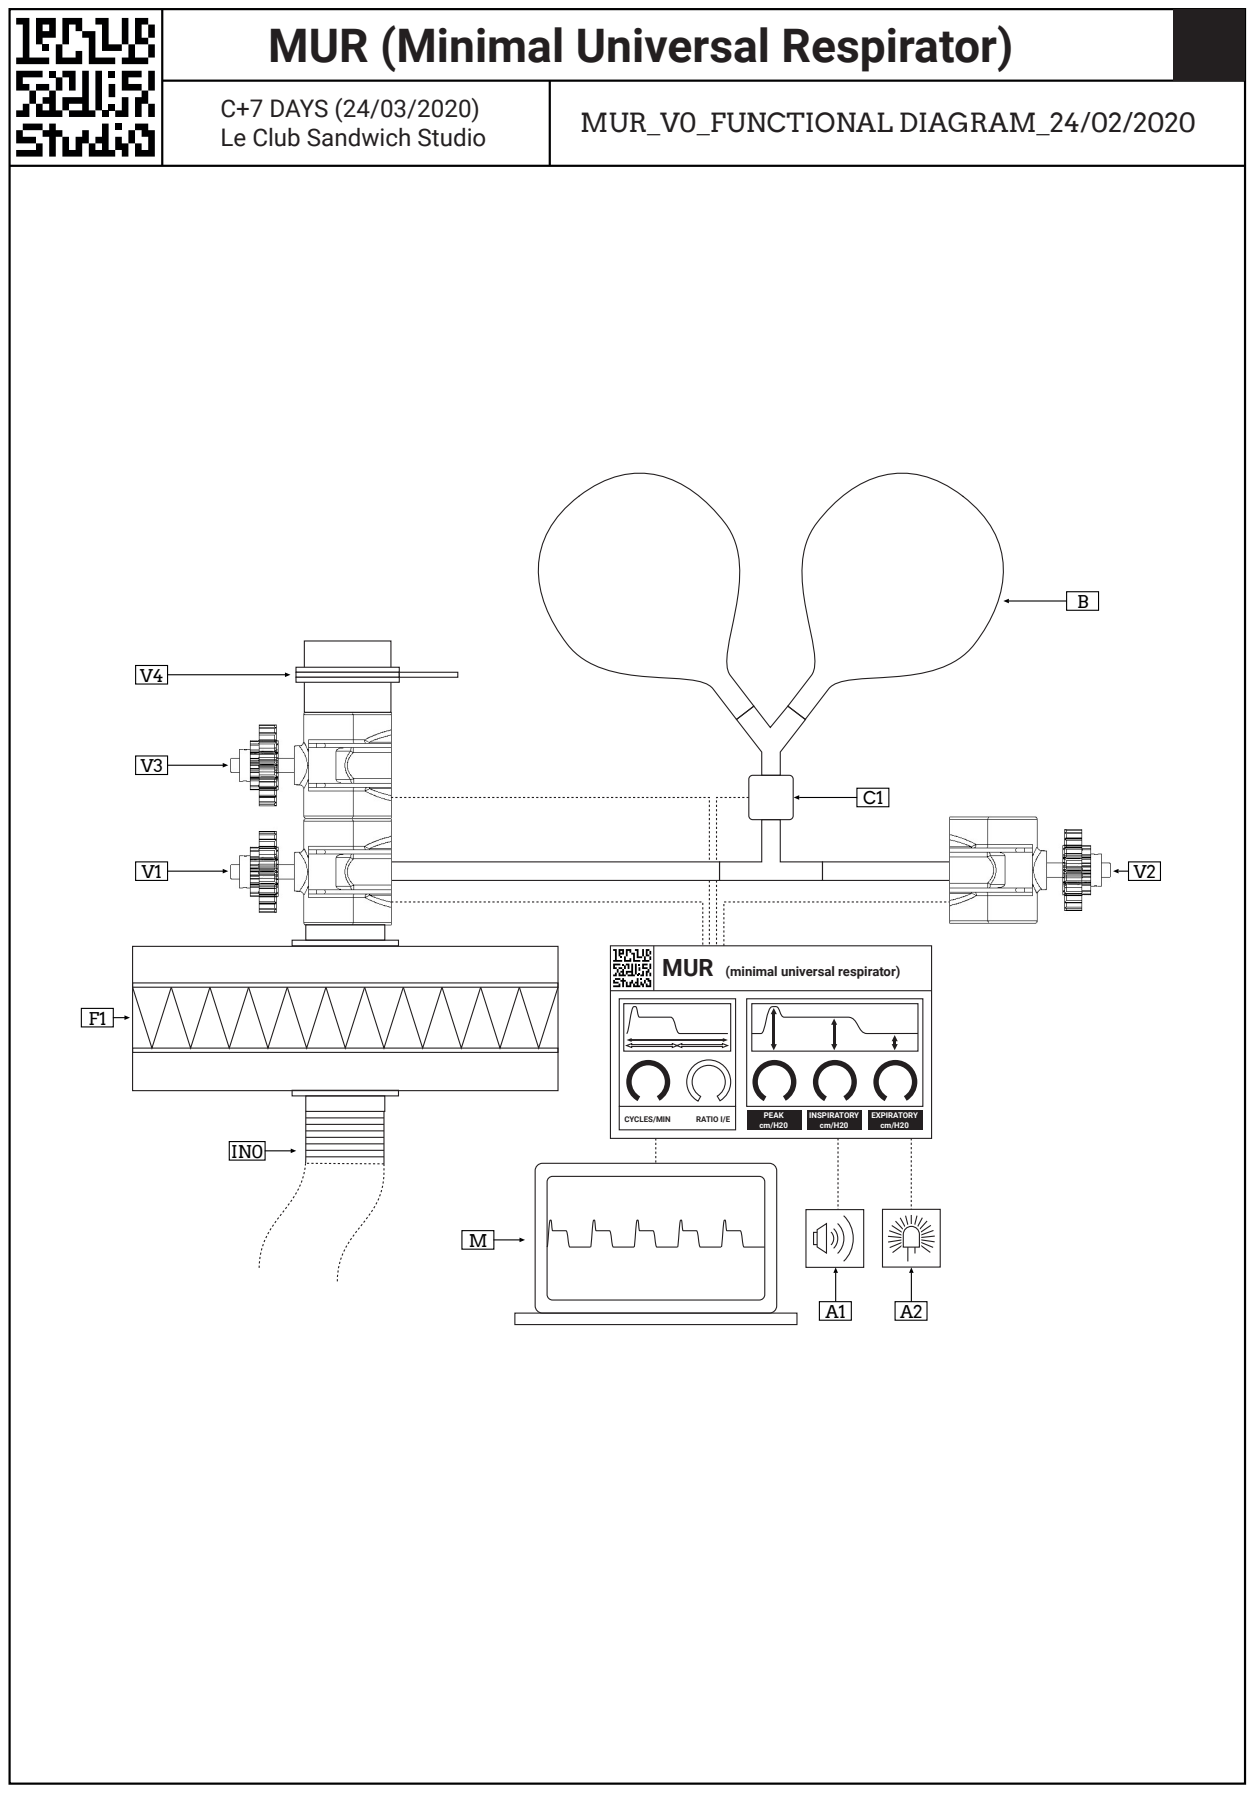
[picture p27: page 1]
CYCLES/MIN; RATIO I/E; PEAK; INSPIRATORY cm/H20; EXPIRATORY cm/H20

MUR (Minimal Universal Respirator)

MUR (minimal universal respirator)

### MUR_V0_FUNCTIONAL DIAGRAM_24/02/2020 C+7 DAYS (24/03/2020) Le Club Sandwich Studio

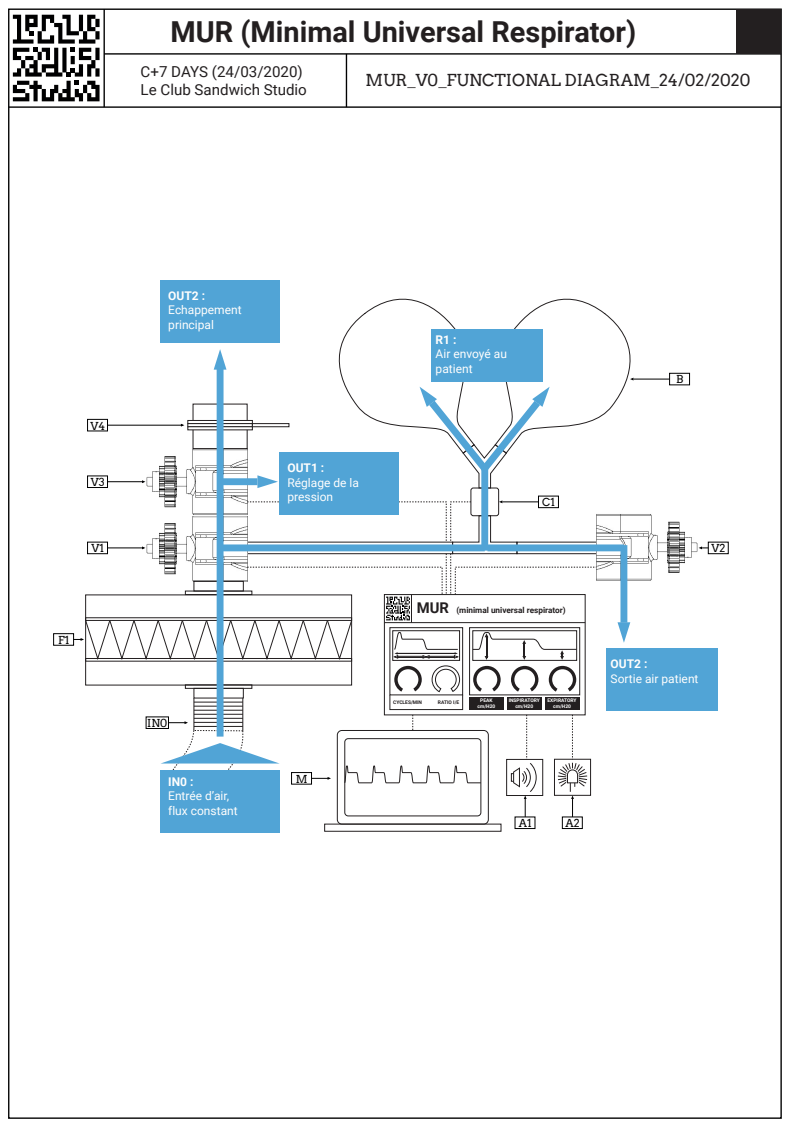
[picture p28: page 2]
CYCLES/MIN; RATIO I/E; PEAK; INSPIRATORY cm/H20; EXPIRATORY cm/H20; IN0 : Entrée d’air, flux constant; OUT1 : Réglage de la pression; OUT2 : Echappement principal; R1 : Air envoyé au patient

MUR (minimal universal respirator)

OUT2 :
Sortie air patient

### MUR_V0_FUNCTIONAL DIAGRAM_24/02/2020 C+7 DAYS (24/03/2020) Le Club Sandwich Studio

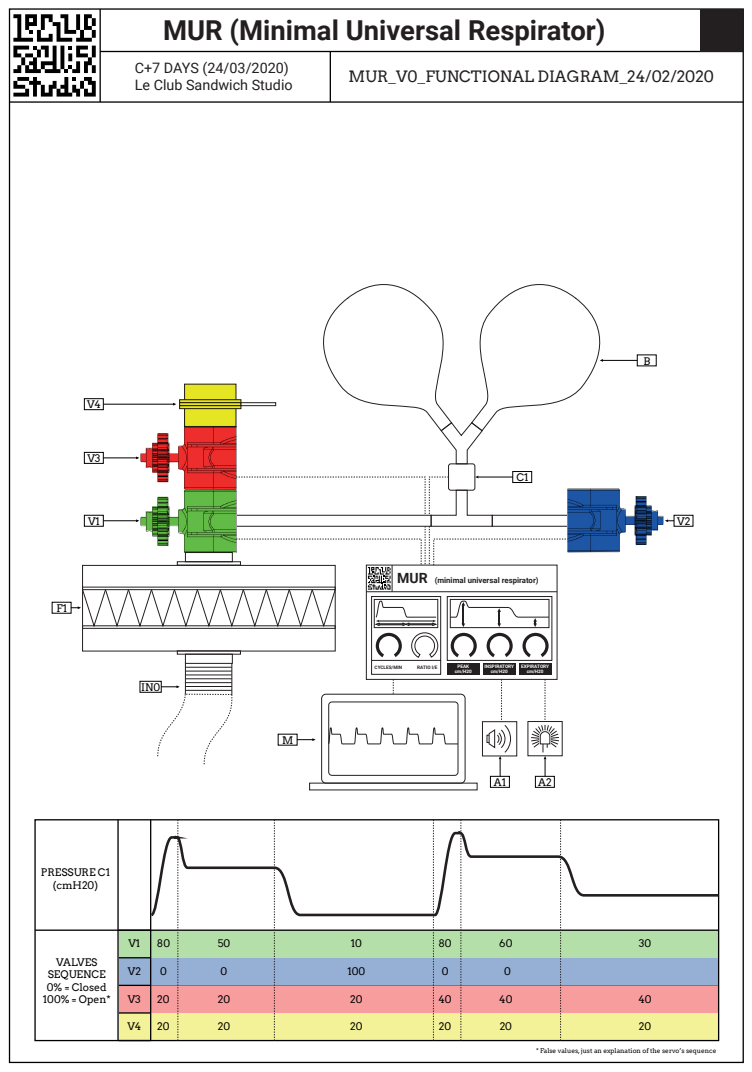
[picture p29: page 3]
CYCLES/MIN; RATIO I/E; PEAK; INSPIRATORY cm/H20; EXPIRATORY cm/H20; IN0 : Entrée d’air, flux constant; OUT1 : Réglage de la pression; OUT2 : Echappement principal; R1 : Air envoyé au patient; PRESSURE C1 (cmH20); VALVES SEQUENCE 0% = Closed 100% = Open*

MUR (minimal universal respirator)

OUT2 :
Sortie air patient

* False values, just an explanation of the servo’s sequence

### MUR_V0_FUNCTIONAL DIAGRAM_24/02/2020 C+7 DAYS (24/03/2020) Le Club Sandwich Studio

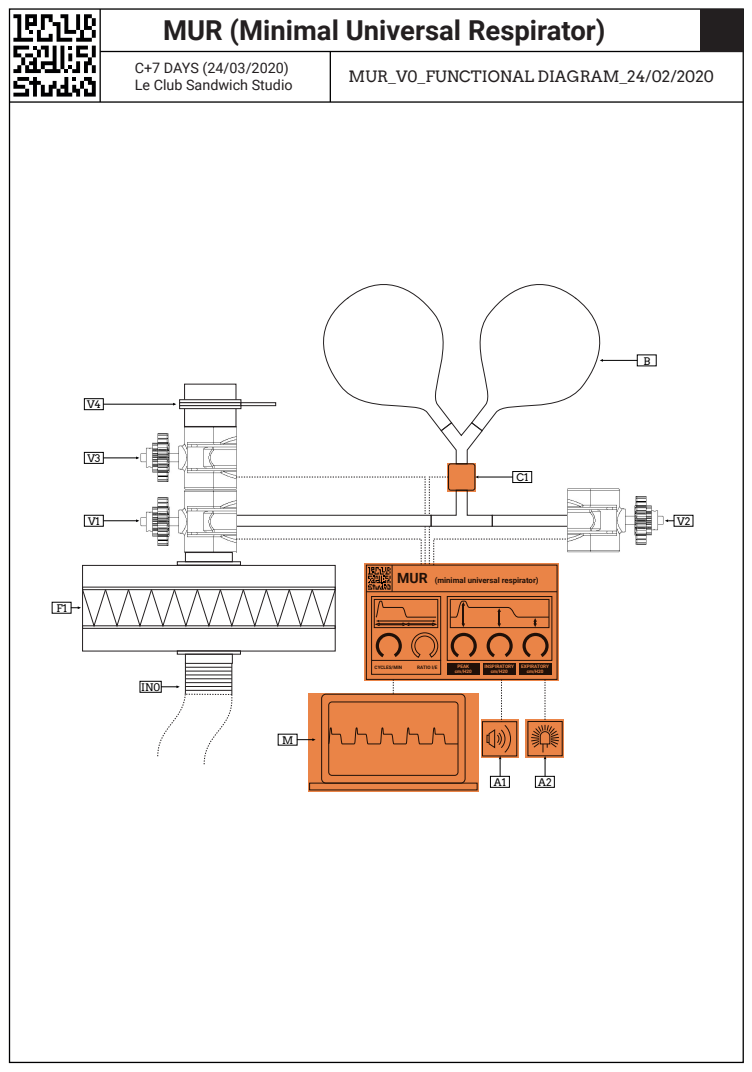
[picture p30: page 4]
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

MUR (minimal universal respirator)

OUT2 :
Sortie air patient

* False values, just an explanation of the servo’s sequence

| Schéma de fonctionnement 1
C+5 DAYS (22/03/2020) Le Club Sandwich Studio | V0 MVP (Minimum Viable Product)

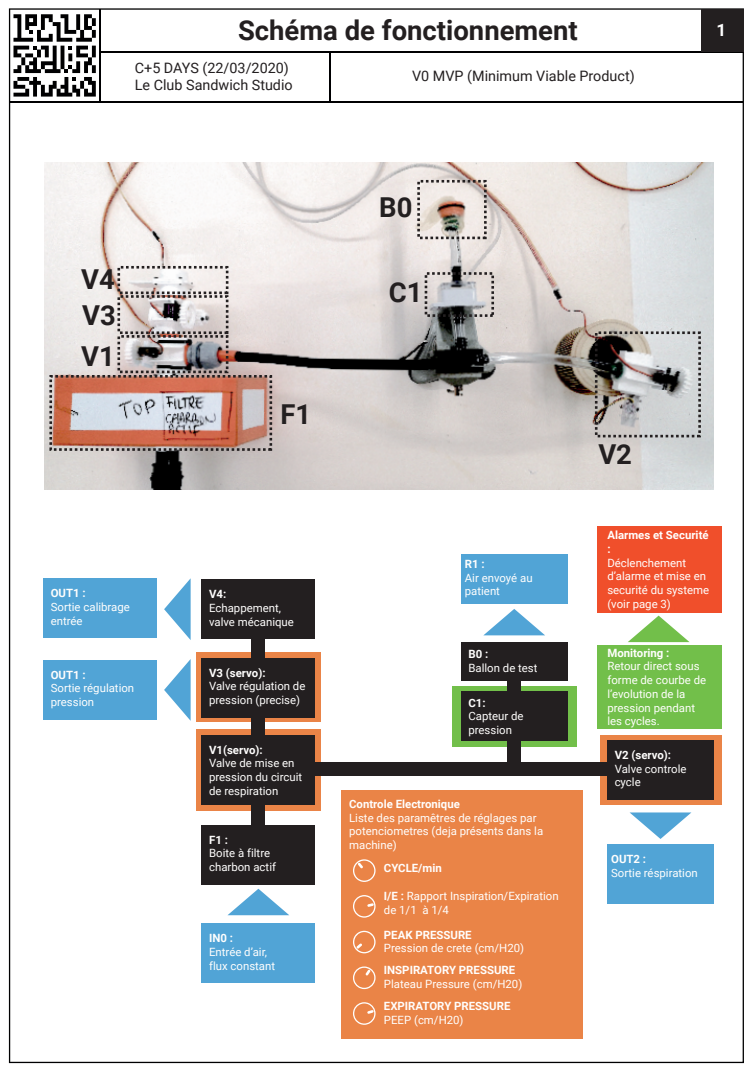
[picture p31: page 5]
F1 : Boite à filtre charbon actif; IN0 : Entrée d’air, flux constant; OUT2 : Sortie réspiration; OUT1 : Sortie régulation pression; OUT1 : Sortie calibrage entrée; V4: Echappement, valve mécanique; V2 (servo): Valve controle cycle; C1: Capteur de pression; R1 : Air envoyé au patient

Alarmes et Securité
Déclenchement
d’alarme et mise en
securité du systeme
(voir page 3)

Ballon de test

Monitoring :
Retour direct sous
forme de courbe de
l’evolution de la
pression pendant
les cycles.

V3 (servo):
Valve régulation de
pression (precise)

V1(servo):
Valve de mise en
pression du circuit
de respiration

Controle Electronique
Liste des paramêtres de réglages par
potenciometres (deja présents dans la
machine)
CYCLE/min
I/E : Rapport Inspiration/Expiration
PEAK PRESSURE
Pression de crete (cm/H20)
INSPIRATORY PRESSURE
Plateau Pressure (cm/H20)
EXPIRATORY PRESSURE
PEEP (cm/H20)

| Rapport de test Pression (C1) 2
Le Club Sandwich Studio | Cycles de respiration et courbes de pression

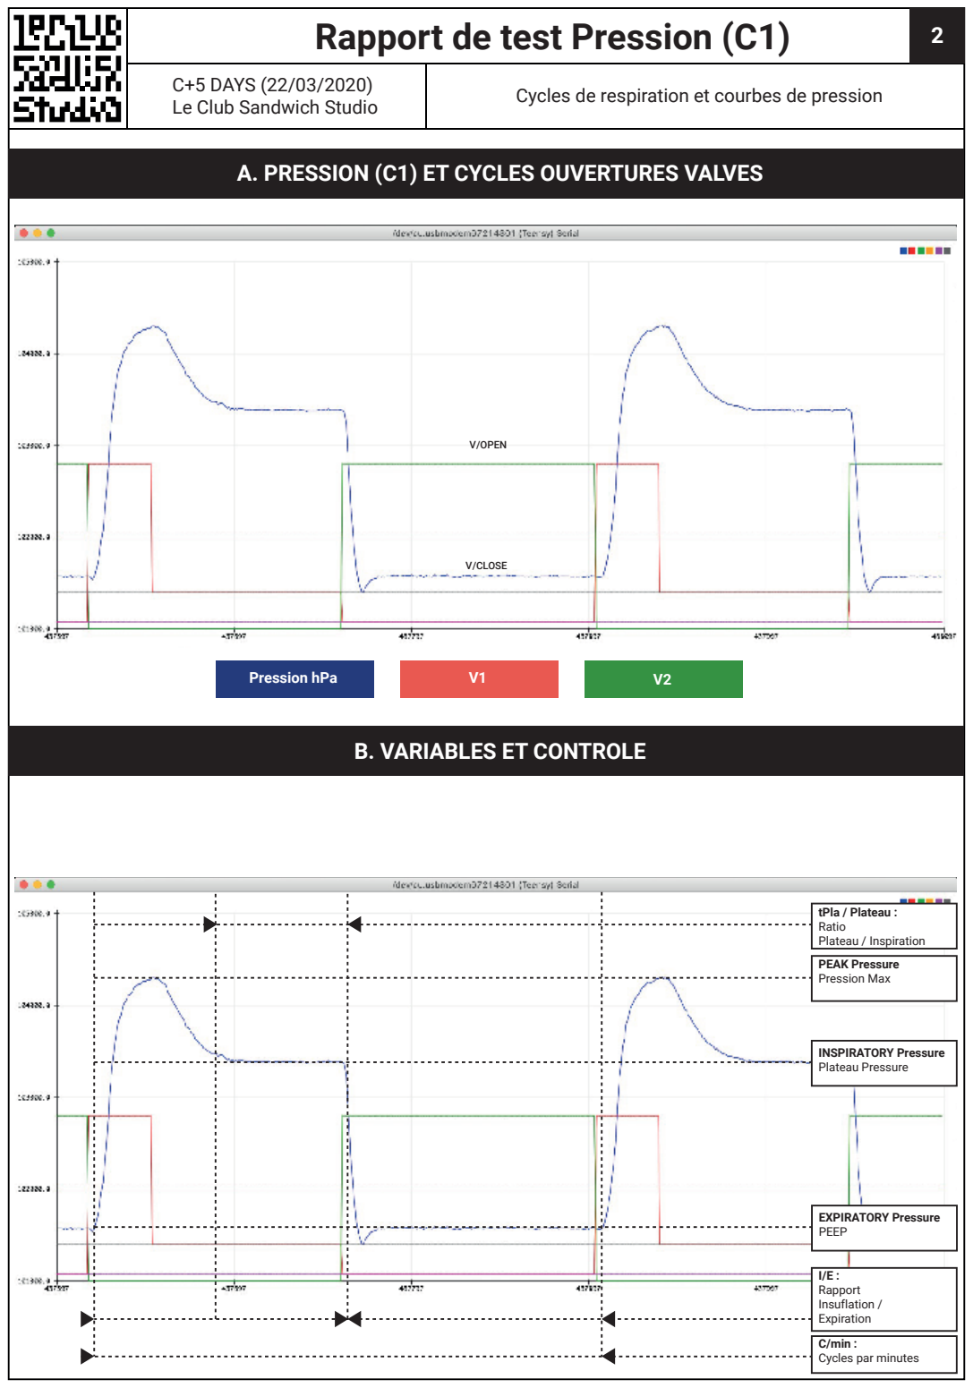
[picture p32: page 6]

INSPIRATORY Pressure
Plateau Pressure
Pression hPa | V1 | V2

V/OPEN

V/CLOSE

C/min :
Cycles par minutes

I/E :
Rapport
Insuflation /
Expiration

PEAK Pressure
Pression Max

tPla / Plateau :
Ratio
Plateau / Inspiration

## A. PRESSION (C1) ET CYCLES OUVERTURES VALVES

## B. VARIABLES ET CONTROLE

EXPIRATORY Pressure
PEEP

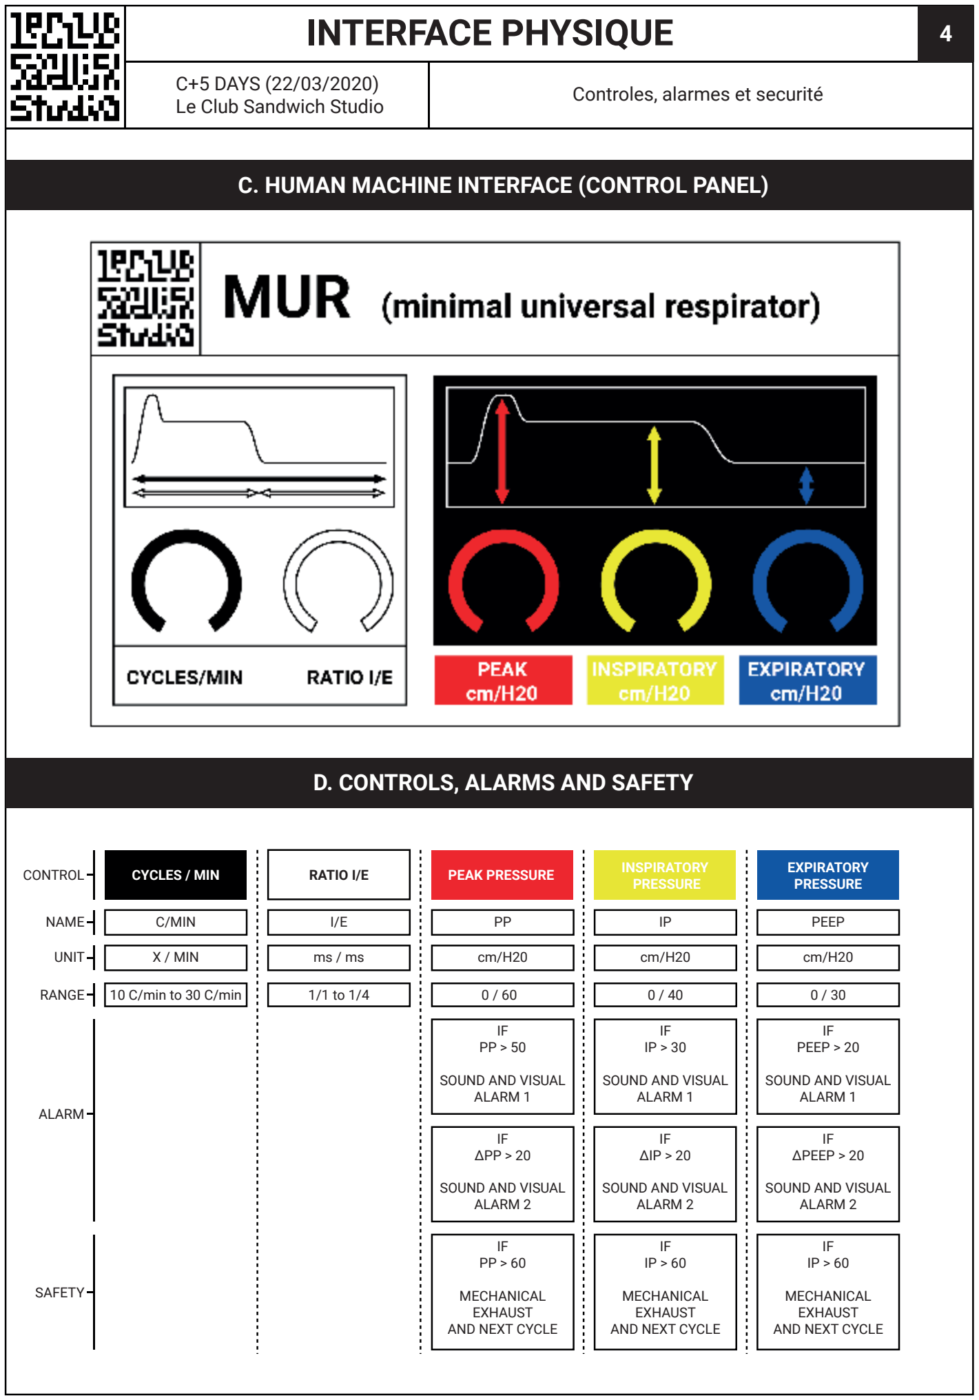
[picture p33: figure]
INTERFACE PHYSIQUE 4; PRESSURE; EXPIRATORY PRESSURE; X / MIN; SOUND AND VISUAL ALARM 1; SOUND AND VISUAL ALARM 2; IF ∆PEEP > 20; MECHANICAL EXHAUST AND NEXT CYCLE; IF PEEP > 20; NAME; C/MIN; CONTROL; UNIT; RANGE; ALARM; SAFETY; PEEP; D. CONTROLS, ALARMS AND SAFETY

Le Club Sandwich Studio | Controles, alarmes et securité
CYCLES / MIN | RATIO I/E | PEAK PRESSURE | INSPIRATORY
10 C/min to 30 C/min | 1/1 to 1/4 | 0 / 60 | 0 / 40 | 0 / 30

## C. HUMAN MACHINE INTERFACE (CONTROL PANEL)

| INTERFACE PHYSIQUE 3
Le Club Sandwich Studio | Proposition de conception simple

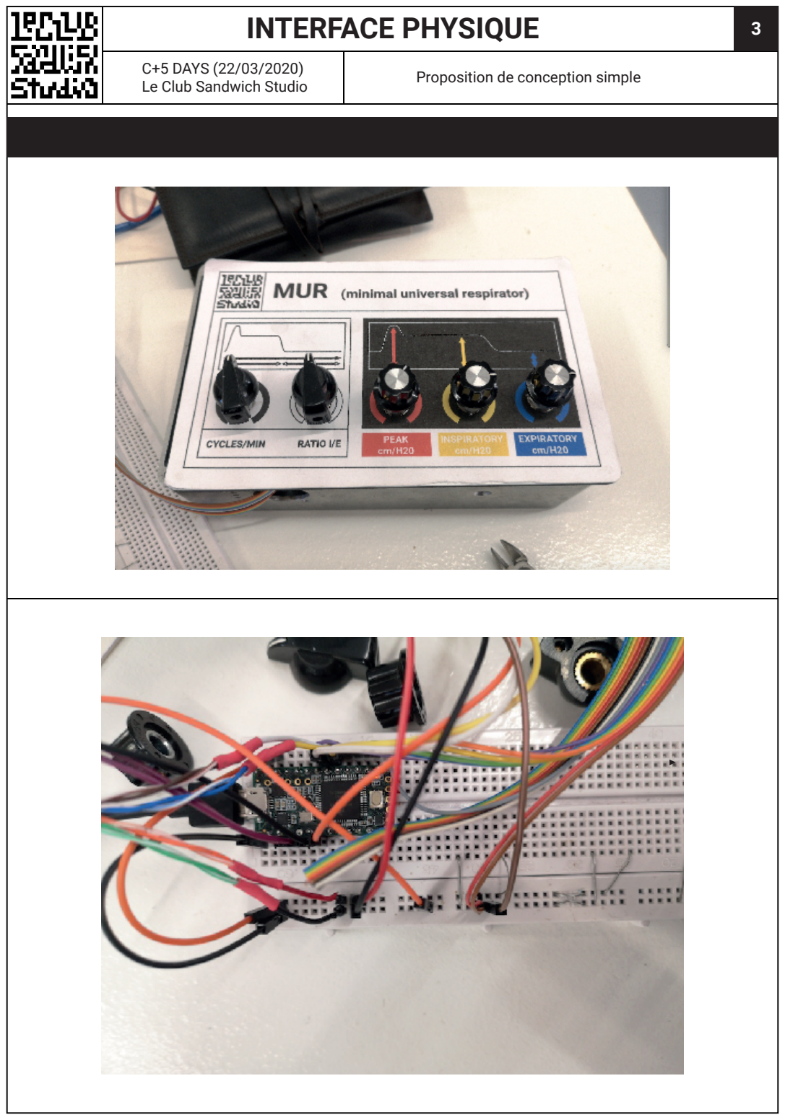
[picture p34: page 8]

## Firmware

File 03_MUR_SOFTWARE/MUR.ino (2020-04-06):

/***************************************************************************
  Copyright 2020 LE CLUB SANDWICH STUDIO SAS

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
    You should have received a copy of the GNU General Public License
    along with this program.
***************************************************************************/

/***************************************************************************
  !!!                        DISCLAMER                                 !!!
  ALARMS ARE NOT JET WORKING PROPERLY DUE TO TWO REASONS :
  - BME280 library is blocking the loop if the sensor fails
  - I didn't untangle all the program flow...

  BUT :
  It beeps when you exceed peakAlarmLevel and plateauAlarmlevel
  This provides a minimum of over pressure protection...
***************************************************************************/

#include <Servo.h>
#include <Wire.h>
#include <Adafruit_BME280.h>

Servo inValve;
Servo outValve;
Adafruit_BME280 bmePatient;
Adafruit_BME280 bmeAmbient;

// Servo Calibration, Alarm Levels and flags

/***************************************************************************
  //  THERE IS NO "STANDARD SERVO OR AIRSOURCE" IN THIS PROJECT FOR INSTANCE
  //  DUE TO THE DIFFICULTY TO GET RELIABLY PARTS DURING LOCKDOWN
  //  
  //  !!! WE ARE USING FUTABA S3003 SERVOS IN THIS PROTOTYPE with V2.1 VALVES !!!
  //
  //  Please follow the steps carefully to calibrate your device to
  //  your Servos and Airsource. Wrong calibration can be harmful or even
  //  kill a person! If you run into problems :
  //  Common sense, physics and anatomy knowledge may help!
  //
  //
  //  1. Mount and calibrate Valves :
  //
  //  - !!! DON'T MOUNT ANY SERVO IN THE VALVES !!! You could damage the valves
  //  - Plug the servos and power up the device
  //  - enable the maintaince switch so that the servo goes to 0° (closed valven position)
  //  - close the Valve by Hand and check for air tight
  //  - reapeatly check for easy-moving and air tight
  //  - Mount the servos into the valves
  //  - disable Maintaince Switch and check for each valve if they are air tight
  //  - your system usually has leaks due to 3d printing
  //  tolerance. make shure they are as small as possible!
  //
  //
  //  2. Calibrate absolute Pressure from Airsource and Servo movement :
  //
  //  - Connect all "plumbing" to the device.
  //  - Close the patient side hole with something air tight!
  //  - Open overpressure Valve (V3) on the filterbox
  //  - engage maintaince and calibration Switches
  //  - Power up the device, WITHOUT AIRSOURCE!
  //  - inValve should open, outValve is closed
  //  - power up or connect your Airsource
  //  - Open Arduino Serial Plotter
  //  - adjust the overpressure valves until reach the desired pressure
  //  (usually i close almost completly the little valve and I progressifly close 
  //  the valve on the filter box...)
  //  - switch back maintaince and calibration Switches to normal position
  //  - control pressure levels over several cycles and adjust if necessary
  //  - play with the controls, be shure the pressure is ok, check peak, plateau 
  //  and expiratory individually
  //  - if the valves open to wide, lower the servoCal value (less servo wear), 
  //  - if the pressure is to low rise the servoCal Value 
  //  (carefully! your servo will wear more)
  //
  //  BE SURE THAT YOUR AIRSOURCE IS STABLE OVER TIME, WE OBSERVED THAT 
  //  TURBINE AIRSOURCES LOSE MORE POWER ONCE HOT THAN MEMBRANE PUMPS
  //
  //  !!! ATTENTION THIS A MEDICAL DEVICE, YOUR JOB AS MAKER IS ONLY TO MAKE 
  //  AND CALIBRATE THE DEVICE, NOT TO OPERATE THE DEVICE !!!
***************************************************************************/

//  Please adapt these three values to your Servos and Airsource. We use Futaba S3003 Servos.
int servoCal = 50;          // maximum movement of servo
int inValveLatency = 30;    // close the inValve slightly before opening outValve
int outValveLatency = 200;  // close the outValve slightly before opening outValve

// treshold values are arbitary set after consulting wikipedia. minimum 600hpa, maximum 1200hpa
float minimumAtmosphericPressure = 600.;
float maximumAtmosphericPressure = 1200.;
// Ring Alarm if differential Pressure goes above that
float peakAlarmLevel = 40.;
float plateauAlarmLevel = 30.;
bool peakAlarm = 0;
bool plateauAlarm = 0;

// Potentiometer and Servo pins
int inValvePin = 2;     // Pin for input Valve
int outValvePin = 3;    // Pin for Output Valve
int Led = 5;            // future neopixel Led for user feedback
int Buzzer = 6;         // Alarm Buzzer
int Maintenance = 7;    // sets all valves to 0° for maintaince
int PressureCal = 8;  // closes outputValve and opens Input Valve for maximum pressure calibration
int Cycles = A0;
int Ratio = A1;
int Peak = A6;
int Inspiratory = A7;
int Expiratory = A8;

// different timers in our breathing cycle
unsigned long cycle = 0;
unsigned long peakT = 0;
unsigned long plateauT = 0;
unsigned long expirationT = 0;

// running timers to get asycronous loop
unsigned long cycleZero = 0;
unsigned long bmpZero = 0;

//running cycle flags
bool peak = 0;
bool plateau = 0;
bool expiration = 0;

// Servo positions and others
int ivPos = 0;
int ovPos = servoCal;
int pvPos = 0;
int plateauPos = 0;
int baselinePos = 0;
float bmpP = 0.;
float bmeP = 0.;
float differentialP = 0.;
// pressure sensor sample Frequency = 20ms runs smooth on teensy3.2
unsigned long pressureSample = 20;
bool pressureSensorFailure = 0;

// Read all potentiometers and adjust values
void readPot() {
  // calculate total breath cycle lenght
  cycle = map(analogRead(Cycles), 0, 1023, 6000, 2000);
  // calculate the time of the inspiration cycle including plateau
  plateauT = map(analogRead(Ratio), 0, 1023, (cycle / 2), (cycle / 4));
  // add peak if necessairy
  int tempI = analogRead(Peak);
  // impementation of "dead Zone" on the low end of the peak potentiometer
  // the "inValveLatency * 3" is just some rule of thumb, depends heavily on the Servo used
  if (tempI <= (inValveLatency * 3)) {
    peakT = 0;
  } else {
    // inspiration Peak can not go higher than 1/10th of inspiration!
    peakT = map(tempI, 100, 1023, 50, (plateauT / 10));
  }

  // set plateau support pressure
  plateauPos = map(analogRead(Inspiratory), 0, 1023, 0, (servoCal / 3));
  // set baseline pressure, can only be opend until a certain point
  baselinePos = map(analogRead(Expiratory), 0, 1023, 0, (servoCal / 4));
}

void updateSensors() {
  // reset timer first for regular intervals!
  bmpZero = millis();
  // read Sensors, get differential
  bmePatient.takeForcedMeasurement();
  bmpP = (float)bmePatient.readPressure() / 100.;
  bmeAmbient.takeForcedMeasurement();
  bmeP = (float)bmeAmbient.readPressure() / 100.;
  differentialP = bmpP - bmeP;

  // check for sensor failiure, this alarm doesn't care if another alarm is active.
  // this is due to the fact that if one sensor fails the other alarms won't work anymore...
  if ((bmpP <= minimumAtmosphericPressure) || (bmpP >= maximumAtmosphericPressure) || (bmeP <= minimumAtmosphericPressure) || (bmeP >= maximumAtmosphericPressure)) {
    pressureSensorFailure = 1;
    digitalWrite(Buzzer, HIGH);
  }
  // check for realistic pressures if pressureSensorFailure is active
  if (pressureSensorFailure == 1) {
    if ((bmpP > minimumAtmosphericPressure) && (bmpP < maximumAtmosphericPressure) && (bmeP > minimumAtmosphericPressure) && (bmeP < maximumAtmosphericPressure)) {
      pressureSensorFailure = 0;
      digitalWrite(Buzzer, LOW);
    }
  }

  // this is a more userfriendly graph
  Serial.print(differentialP);
  Serial.print("\t");
  Serial.print(ivPos / 4);
  Serial.print("\t");
  Serial.println(ovPos / 4);

  // this is more like a debug graph
  /*Serial.print(bmpP);
    Serial.print("\t");
    Serial.print(bmeP);
    Serial.println("\t");
    // do some funny math to see valve positions on the graphs on Serial Plotter
    // made at about 60m above sea level.
    Serial.print((float)(101000 + (ivPos * 10)) / 100.);
    Serial.print("\t");
    Serial.print((float)(101000 + (ovPos * 10)) / 100.);
    Serial.print('\t');
    Serial.print((float)(101000 + (pvPos * 10)) / 100.);
    Serial.print('\t');
    Serial.print(101000 + (baselinePos * 10));
    Serial.print('\t');
    Serial.println(101000 + (plateauPos * 10));
  */
}

void setup() {
  pinMode(Maintenance, INPUT_PULLUP);
  pinMode(PressureCal, INPUT_PULLUP);
  pinMode(Buzzer, OUTPUT);
  digitalWrite(Buzzer, LOW);
  Serial.begin(115200);
  bool P1 = bmePatient.begin(0x77);
  if (!P1) {
    pressureSensorFailure = 1;
    //Serial.println("Could not find a valid BMP180 sensor, check wiring, address, sensor ID!");
  }
  // configure bme280 : mode, tempSampling, pressSampling, humSampling, filter, duRation
  bmePatient.setSampling(1, 1, 3, 1, 1, 10);
  bool P2 = bmeAmbient.begin(0x76);
  if (!P2) {
    pressureSensorFailure = 1;
    //Serial.println("Could not find a valid BME280 sensor, check wiring, address, sensor ID!");
  }
  bmeAmbient.setSampling(1, 1, 3, 1, 1, 10);
  // if the two pressure sensors are started for good light the led in green, attach servos and wait a bit
  inValve.attach(inValvePin);
  outValve.attach(outValvePin);
  inValve.write(ivPos);
  outValve.write(ovPos);
  readPot();
}
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

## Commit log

2020-03-25 V0 Publication
    - Add software
    - Add hardware schematic
    - Add basic general functional schemas
    - Add 3D models
    - Update general licence
    [Adaptor_X3.stl, MUR_V0.1_Wiring.sch, Pinion_20.stl, Spur_40.stl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]
2020-03-27 Add Arduino Code for 2 valve version, try to better organize all that stuff
2020-03-29 better calibration procedure and other improvements
    [MUR_V0.1_Wiring.sch]
2020-03-29 rename folder to actual version V0.1
    [Adaptor_X3.stl, MUR_V0.1_Wiring.sch, Pinion_20.stl, Spur_40.stl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]
2020-03-30 Update 3D files
    Update and classification of V1.0 V2.0 and V2.1
    [Adaptor_X2.stl, Adaptor_X3.stl, Pinion_20.stl, Spur_40.stl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]
2020-03-31 Update with main hole diameter at 23.30
    Correction and simplification over different versions
    [Adaptor_X2.stl, Pinion_20.stl, ServoHolder.stl, Servo_Lever.stl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]
2020-03-31 Adapting code to updated Prototype
2020-04-06 full repo reorg for next set of documents (#12)
    * cleanup
    * source code under GPLv3 as the whole project
    * remove .DS_Store
    * reorganize repo
    * reorganize repo
    * reorg ASL5000 tests
    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
    [Adaptor_X2.stl, Adaptor_X3.stl, MUR_V0.1_Wiring.sch, Pinion_20.stl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]
2020-04-07 Overview v0.3 (#13)
    * tests README
    * LICENCE cleanup
    * more to read
    * more reorg
    * reorg tests
    * models re-versionning
    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
    [Adaptor_X2.stl, Adaptor_X3.stl, Pinion_20.stl, ServoHolder.stl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]

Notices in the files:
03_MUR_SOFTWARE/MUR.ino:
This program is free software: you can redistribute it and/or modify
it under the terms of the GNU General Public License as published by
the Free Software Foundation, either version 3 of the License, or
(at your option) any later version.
